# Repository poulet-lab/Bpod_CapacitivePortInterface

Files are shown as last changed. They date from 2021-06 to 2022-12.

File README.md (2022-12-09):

# Capacitive Port Interface for Bpod State Machine

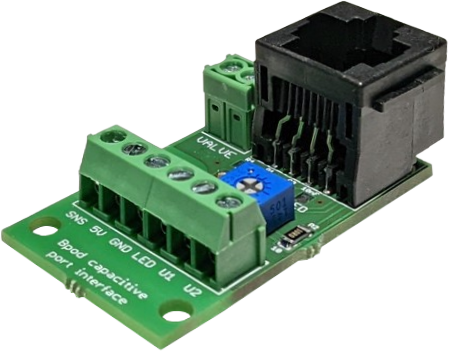
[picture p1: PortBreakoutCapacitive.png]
A drop-in replacement for the [regular port interface](https://www.sanworks.io/shop/viewproduct?productID=1004) enabling for capacitive sensing of lick events. Connect a metal lickspout with a short piece of wire to the SNS port of the interface. Baseline calibration will be performed upon power-on - it can be triggered by briefly unplugging the port interface's RJ45 cable from the Bpod's behavior port once everything is in place.

## Bill of Materials
| Item     | Vendor    | Qty | Part Number                                                                                                                        | Description                 |
| :------- | :------   | :-: | :--------------------------------------------------------------------------------------------------------------------------------- | :-------------------------  |
| C1       | Digi-Key  |  1  | [CC1206JRX7R9BB682-ND](https://www.digikey.com/products/en?keywords=CC1206JRX7R9BB682-ND)                                                        | 6.8 nF capacitor (1206)      |
| C2, C3   | Digi-Key  |  2  | [311-1179-2-ND](https://www.digikey.com/products/en?keywords=311-1179-2-ND)                                                        | 100 nF capacitor (1206)     |
| IC1      | Digi-Key  |  1  | [AT42QT1011-TSHRTR-ND](https://www.digikey.com/products/en?keywords=AT42QT1011-TSHRTR-ND)                                          | touch sensor IC             |
| R1       | Digi-Key  |  1  | [13-RC1206FR-1010KLTR-ND](https://www.digikey.com/products/en?keywords=13-RC1206FR-1010KLTR-ND)                                    | 10k ohm resistor (1206)     |
| R2       | Digi-Key  |  1  | [13-RC1206FR-1010RLTR-ND](https://www.digikey.com/products/en?keywords=13-RC1206FR-1010RLTR-ND)                                    | 10 ohm resistor (1206)      |
|          | Digi-Key  |  1  | [3362P-501LF-ND](https://www.digikey.com/products/en?keywords=3362P-501LF-ND)                                                      | 500 ohm trimpot             |
|          | Digi-Key  |  1  | [277-1721-ND](https://www.digikey.com/products/en?keywords=277-1721-ND)                                                            | 2 pos screw terminal	    |
|          | Digi-Key  |  1  | [277-1736-ND](https://www.digikey.com/products/en?keywords=277-1736-ND)                                                            | 4 pos screw terminal	    |
|          | Digi-Key  |  1  | [A31413-ND](https://www.digikey.com/products/en?keywords=A31413-ND)                                                                | Ethernet jack               |
|          | Lee Valve |  1  | [LHDA1231115H](https://www.theleeco.com/products/electro-fluidic-systems/solenoid-valves/control-valves/lhd-series/3-port/ported/) | Solenoid valve              |

The above BOM is for the ```no_user``` version of the PCB. If you want to access the 
extra two lines of the RJ45 connector (like we do at Poulet-Lab) use the respective version of the PCB (```PortBreakoutCapacitive_r*.brd```) and swap the 4 position screw terminal for a 6 position screw terminal ([277-1738-ND](https://www.digikey.com/products/en?keywords=277-1738-ND)).

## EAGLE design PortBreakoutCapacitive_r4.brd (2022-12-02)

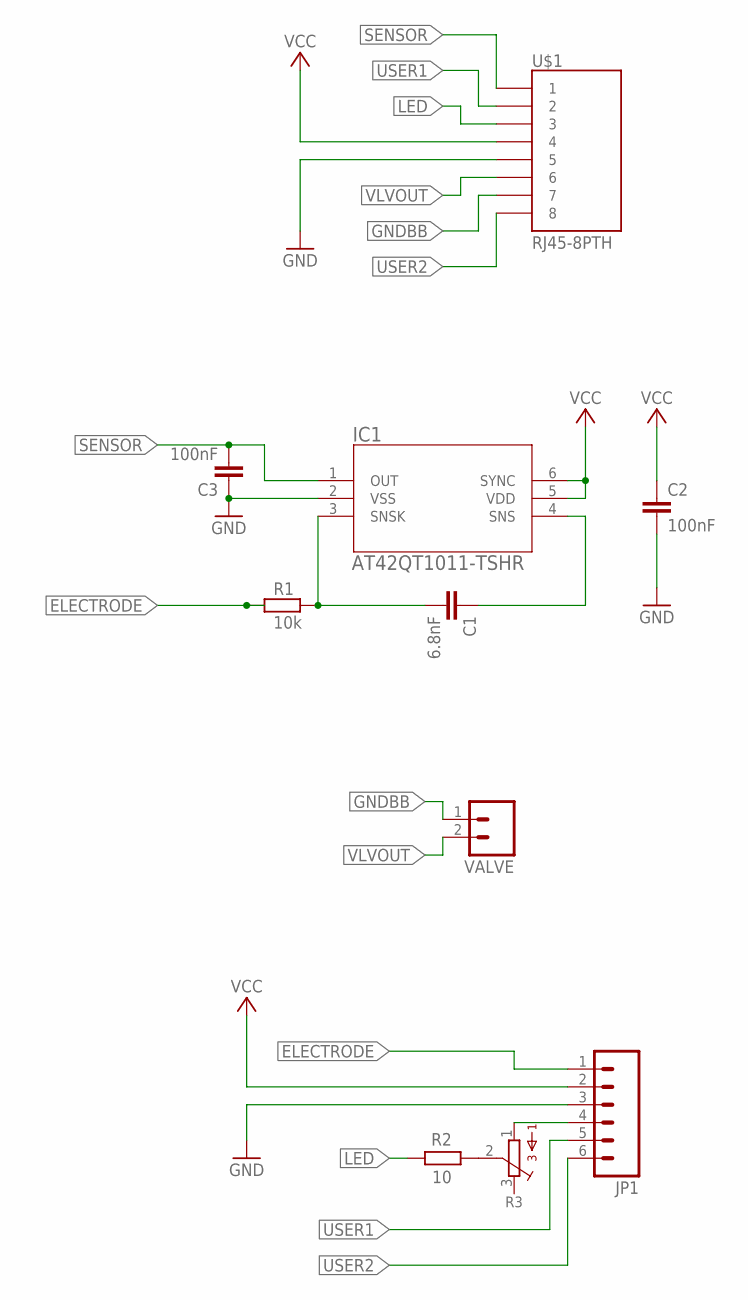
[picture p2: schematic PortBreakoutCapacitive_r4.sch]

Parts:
C1: 6.8nF; C1206
C2, C3: 100nF; C1206
IC1: AT42QT1011-TSHR; 6ST1_ATM
JP1: M063.5MM-6; SCREWTERMINAL-3.5MM-6
R1: 10k; R1206
R2: 10; R1206
R3: 3362R
U$1: RJ45-8PTH; RJ45-8
VALVE: M023.5MM_LOCK; SCREWTERMINAL-3.5MM-2_LOCK

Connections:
ELECTRODE: JP1.1, R1.1
GND: C2.2, C3.1, IC1.2 (VSS), JP1.3, U$1.5
GNDBB: U$1.7, VALVE.1
LED: R2.2, U$1.3
unnamed: R2.1, R3.2
unnamed: JP1.4, R3.1
SENSOR: C3.2, IC1.1 (OUT), U$1.1
SNS: C1.1, IC1.4 (SNS)
SNSK: C1.2, IC1.3 (SNSK), R1.2
USER1: JP1.5, U$1.2
USER2: JP1.6, U$1.8
VCC: C2.1, IC1.5 (VDD), IC1.6 (SYNC), JP1.2, U$1.4
VLVOUT: U$1.6, VALVE.2

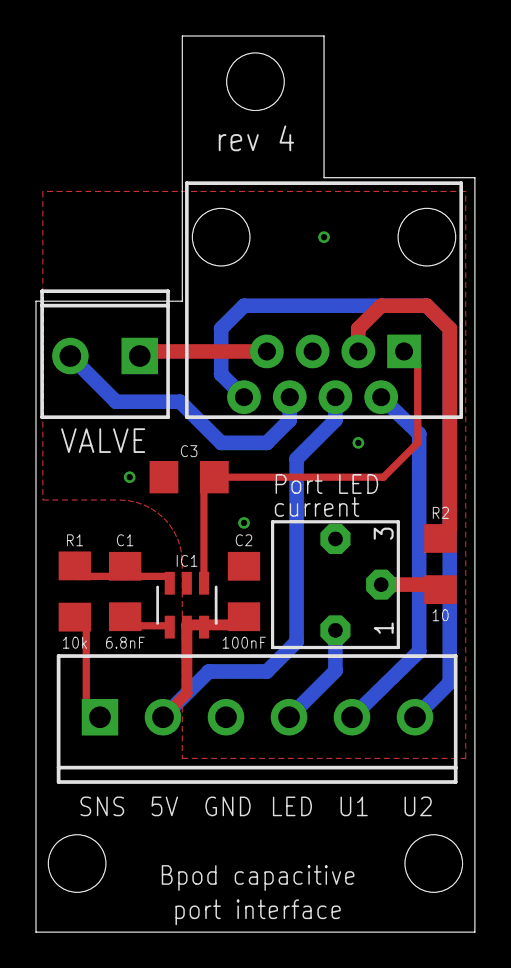
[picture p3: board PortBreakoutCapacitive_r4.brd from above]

Board: 2 copper layers, 24.4 x 49.8 mm, 10 parts (0 on the bottom side), 13 nets.

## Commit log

2021-06-29 revision 2
    [PortBreakoutCapacitive_r2.brd, PortBreakoutCapacitive_r2.sch, PortBreakoutCapacitive_r2_no_user.brd, PortBreakoutCapacitive_r2_no_user.sch]
2022-03-11 Removed transistor Q1
    [PortBreakoutCapacitive_r3.brd, PortBreakoutCapacitive_r3.sch, PortBreakoutCapacitive_r3_no_user.brd, PortBreakoutCapacitive_r3_no_user.sch]
2022-03-11 minor clean-up
    [PortBreakoutCapacitive_r3_no_user.brd, PortBreakoutCapacitive_r3_no_user.sch]
2022-04-19 rev 4: C1 with lower capacitance
    [PortBreakoutCapacitive_r4_no_user.brd, PortBreakoutCapacitive_r4_no_user.sch]
2022-04-19 Revert "rev 4: C1 with lower capacitance"
    This reverts commit f0b3ebc7fd996792bcba9bfe078b693bdcbdf926.
    [PortBreakoutCapacitive_r3.brd, PortBreakoutCapacitive_r3.sch, PortBreakoutCapacitive_r4_no_user.brd, PortBreakoutCapacitive_r4_no_user.sch]
2022-04-19 some changes to trace routing
    [PortBreakoutCapacitive_r4_no_user.brd, PortBreakoutCapacitive_r4_no_user.sch]
2022-12-02 added label "The Poulet Lab" to backside
    [PortBreakoutCapacitive_r4.brd, PortBreakoutCapacitive_r4_no_user.brd]

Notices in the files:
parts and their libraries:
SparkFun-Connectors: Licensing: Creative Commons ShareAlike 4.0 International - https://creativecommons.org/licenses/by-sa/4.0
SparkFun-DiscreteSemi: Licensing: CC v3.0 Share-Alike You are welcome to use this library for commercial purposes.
